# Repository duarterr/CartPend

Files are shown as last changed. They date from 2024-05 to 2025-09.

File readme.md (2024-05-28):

# Pendulum on a Cart Project

Welcome to the Pendulum on a Cart project repository! This project involves designing, modeling, and controlling a pendulum attached to a cart. The system is a classic example of a dynamic system that can be used to explore control theory and robotics concepts.

## Repository Structure

The repository is organized into the following folders:

- **Design Files**: Contains the Fusion360 model and other related files for the physical construction of the pendulum on a cart.
- **Matlab**: Contains scripts for modeling the system, validating the model, and designing the controller.
- **CodeComposerStudio**: Contains code for the TivaC TM4C123GH6PM microcontroller used to implement the control algorithms.
- **References**: Contains useful references that provide the theoretical background for the project.

## Contents

### Design Files

This directory contains all the necessary files for the physical design and construction of the pendulum on a cart. 

- **Fusion360 Model**: The 3D model of the pendulum on a cart created using Autodesk Fusion360.
- **Additional Design Files**: Other files related to the physical construction of the device, such as drawings, part lists, and assembly instructions.

### Matlab

This directory contains MATLAB scripts and resources for various stages of the project:

- **A_Model_Pend_Estimation.m**: Estimates the pendulum model based on experimental data gathered from the device via UART.
- **B_Model_Pend_Validation.m**: Compares the pendulum model with a set of experimental observations.
- **C_Model_Full_Validation.m**: Validates the entire model (pendulum plus cart) by comparing it with experimental data.
- **D_LQR.m**: Designs an LQR (Linear-Quadratic Regulator) controller for the system.

The directory also includes the following subfolders:

- **Datasources**: Contains the experimental data obtained from the device via UART.
- **Functions**: Contains miscellaneous MATLAB functions used in the scripts.
- **Results**: Stores the results from the scripts.

### CodeComposerStudio

This directory contains the code for the TivaC TM4C123GH6PM microcontroller used in the project.

Many functions from [this repository](https://github.com/duarterr/CodeComposerStudio-Libs) are used.

### References

This directory contains references that provide theoretical background and additional information about the pendulum on a cart system.

## Contributions

Contributions to the project are welcome! If you have any improvements or new features to add, please follow these steps:

1. Fork the repository.
2. Create a new branch (`git checkout -b feature-new-feature`).
3. Commit your changes (`git commit -am 'Add new feature'`).
4. Push to the branch (`git push origin feature-new-feature`).
5. Create a new Pull Request.

## License

Anyone is free to use and modify the contentes of this repository, but please provide credit to the author, Renan Duarte.

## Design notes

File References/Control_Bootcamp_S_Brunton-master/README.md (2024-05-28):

# Control_Bootcamp_S_Brunton
Matlab Code by Steven Brunton on his Control Bootcamp Lessons

UTILITIES

cartpend.m           — system of ODEs for inverted pendulum on a cart

drawcartpend.m       — draw inverted pendulum on cart

drawcartpend_bw.m    — draw with inverted colors

PRELIMINARIES

linearize_cartpend.m — test linearized dynamics

sim_cartpend.m       — simulate nonlinear dynamics

CONTROL AND ESTIMATOR DESIGN

poleplace_cartpend.m — pole placement for controllable system

lqr_cartpend.m       — design LQR full-state feedback controller

obsv_cartpend.m      - test observability

kf_cartpend.m        - design Kalman filter for full-state estimation

Simulink implementations of LQR and LQG in folder “simulink_LQR_LQG”

lqg_simulinkINIT.m   — initializes LQR feedback gains and Kalman filter system

lqr_cartpend_sim.slx — simulink model for LQR

lqg_cartpend_sim.slx — simulink model for LQG

cartpend_sim.*       — system block for inverted pendulum on cart

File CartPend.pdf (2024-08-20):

Modelagem Dinamica de um P ˆ | endulo Invertido em um ˆ

# Carro

### Renan Duarte

### 17 de agosto de 2024

Resumo

Este documento apresenta a modelagem dinamica de um p ˆ | endulo invertido montado em um ˆ
carro, um sistema classico utilizado para testar t ´ | ecnicas de controle devido ´ | a sua complexidade `
nao linear. O objetivo principal ˜ | e manter o p ´ | endulo equilibrado na posic¸ ˆ | ao vertical, utilizando ˜

a forc¸a aplicada ao carro como entrada de controle. O documento inicia com a modelagem do

carro, simplificando o problema ao considerar a acelerac¸ao como entrada direta. A modelagem ˜

do pendulo ˆ | e abordada em seguida, com a linearizac¸ ´ | ao das equac¸ ˜ | oes n ˜ | ao lineares para facilitar ˜
a analise. Finalmente, os modelos do carro e do p ´ | endulo s ˆ | ao combinados em um sistema com- ˜

pleto representado no espac¸o de estados. As matrizes de estado sao derivadas e apresentadas, ˜

oferecendo uma visao integrada das din ˜ | amicas do carro e do p ˆ | endulo. Esta abordagem permite ˆ

a analise e o desenvolvimento de controladores para o sistema integrado, fornecendo uma base ´

solida para a implementac¸ ´ | ao de estrat ˜ | egias de controle. ´

## 1 Introduc¸ao˜

O estudo do pendulo invertido montado sobre um carro (IPC) ˆ | e um problema cl ´ | assico em sistemas ´
dinamicos e controle, exemplificando um sistema n ˆ | ao linear com m ˜ | ultiplos graus de liberdade. Este ´
tipo de sistema e frequentemente utilizado para testar e demonstrar t ´ | ecnicas de controle devido ´ | a sua `
dinamica complexa e n ˆ | ao linear. O sistema consiste em um p ˜ | endulo de comprimento ˆ | l e massa m

montado em um carro que se move ao longo de um eixo horizontal. A posic¸ao do carro no eixo ˜

horizontal e denominada ´ | p e o angulo do p ˆ | endulo em relac¸ ˆ | ao˜ a vertical ` | e denotado por ´ | θ, conforme

apresentado na Figura 1.

O objetivo e manter o p ´ | endulo equilibrado na posic¸ ˆ | ao vertical usando a forc¸a atuante no carro ˜ | u

no eixo horizontal como entrada de controle.

m

θ l

p = 0

p

z | u

z = 0

M

Figura 1: Pendulo Invertido em um Carro ˆ

A modelagem desse sistema e fundamental para entender sua din ´ | amica, prever o comportamento ˆ
do pendulo e desenvolver controladores eficientes para estabiliz ˆ | a-lo. ´

## 2 Modelo matematico do carro ´

### 2.1 Equac¸ao do movimento ˜

Vamos iniciar a modelagem pelo carro que suporta o pendulo. Consideramos que o carro se move ˆ

ao longo de um eixo horizontal e que sua dinamica ˆ | e governada pela segunda lei de Newton. ´
A equac¸ao do movimento do carro ˜ | e dada por (1). ´

M

d

2p
dt²
= Fa + Fr − Fp | (1)

Onde:

- p e a posic¸ ´ | ao do carro no eixo horizontal [m]. ˜
- M e a massa do carro [kg]. ´
- Fa e a forc¸a resultante da acelerac¸ ´ | ao aplicada ao carro [N]. ˜
- Fr e a soma das forc¸as resistivas, incluindo o atrito e a resist ´ | encia do ar [N]. ˆ
- Fp e a forc¸a horizontal exercida pelo p ´ | endulo no ponto de suporte, que depende do ˆ | angulo ˆ | θ e

da velocidade angular ω [N].

Modelar os coeficientes que afetam o movimento do carro, como o atrito entre o carro e o trilho,

a resistencia do ar, e as interac¸ ˆ | oes din ˜ | amicas com o p ˆ | endulo, pode ser uma tarefa complexa e sujeita ˆ
a incertezas. Esses coeficientes sao influenciados por diversos fatores, como variac¸ ˜ | oes na superf ˜ | ´ıcie
do trilho, mudanc¸as nas condic¸oes ambientais, e at ˜ | e mesmo a forma como o p ´ | endulo oscila. Devido a ˆ

essa complexidade, obter valores precisos para esses coeficientes pode ser desafiador e pode introduzir

erros no modelo.

Para simplificar a modelagem do movimento do carro, consideramos como entrada (ou variavel ´

de controle) a acelerac¸ao˜ a, que e aplicada diretamente ao carro. Essa suposic¸ ´ | ao˜ e razo ´ | avel quando o ´

sistema possui um motor com torque suficiente para impor a acelerac¸ao desejada, sem que as forc¸as re- ˜

sistivas interfiram significativamente. Com essa simplificac¸ao, podemos focar na an ˜ | alise da din ´ | amica ˆ
do carro em resposta a acelerac¸ ` | ao aplicada, sem a necessidade de modelar explicitamente as forc¸as ˜
de propulsao e resist ˜ | encia que poderiam complicar o sistema. ˆ

### 2.2 Representac¸ao em espac¸o de estados ˜

Para modelar o comportamento do carro em espac¸o de estados, devemos primeiro definir os es-

tados do sistema, que sao as vari ˜ | aveis necess ´ | arias para descrever completamente sua din ´ | amica em ˆ

qualquer instante de tempo. No caso do carro, podemos escolher os seguintes estados:

- x1 = p: A posic¸ao do carro ao longo do eixo horizontal [m]. ˜
- x2 = v = dp/dt = ˙p: A velocidade do carro [m/s].
Esses dois estados, x1 e x2, sao suficientes para capturar a din ˜ | amica do movimento do carro. ˆ
Utilizando a simplificac¸ao mencionada anteriormente, (1) pode ser reescrita em func¸ ˜ | ao das vari ˜ | aveis ´

de estado do sistema como (2).

x˙2 = a | (2)

A forma geral do modelo de espac¸o de estados e:´

x˙c = Acxc + Bcu | (3)

Onde:

- xc =

h
x1 x2

i⊤
=

h

p vi⊤
e o vetor de estados. ´
- u = a e a entrada do sistema (a acelerac¸ ´ | ao do carro). ˜
- Ac e a matriz que descreve a din ´ | amica do sistema. ˆ
- Bc e a matriz que relaciona a entrada com os estados do sistema. ´

Assim, a reescrita das equac¸oes dos estados na forma matricial resulta nas matrizes ˜ | Ac e Bc dadas
em (4). O modelo dinamico do carro em espac¸o de estados ˆ | e apresentado em 5). ´

Ac =

0 1

0 0

- , Bc =

0

1

- (4)

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
- a | (5)
Essas matrizes capturam a dinamica do carro no espac¸o de estados. A matriz ˆ | Ac define como

os estados do sistema evoluem ao longo do tempo, enquanto a matriz Bc descreve como a entrada

(acelerac¸ao˜ a) influencia os estados.

3 Modelagem matematica do p ´ | endulo ˆ

### 3.1 Equac¸ao do movimento ˜

A equac¸ao do movimento do p ˜ | endulo pode ser derivada a partir do princ ˆ | ´ıpio de conservac¸ao do ˜

momento angular e das forc¸as atuantes no sistema. As principais forc¸as que afetam o movimento do

pendulo incluem a forc¸a gravitacional, a forc¸a de atrito, a resist ˆ | encia do ar e a forc¸a de Coulomb. ˆ

Considerando a soma dos torques em torno do ponto de rotac¸ao e aplicando a segunda lei de ˜

Newton para rotac¸oes, a equac¸ ˜ | ao do movimento do p ˜ | endulo ˆ | e dada por (12). ´

I

d

2
θ
dt²
= τg − τd − τdr − τc + τa | (6)
Essa equac¸ao diferencial n ˜ | ao linear representa a din ˜ | amica angular do p ˆ | endulo em relac¸ ˆ | ao ao ponto ˜

de rotac¸ao, onde: ˜

- θ e o ´ angulo do p ˆ | endulo em relac¸ ˆ | ao˜ a vertical [rad]. `
- I e o momento de in ´ | ercia do p ´ | endulo em relac¸ ˆ | ao ao ponto de rotac¸ ˜ | ao [ ˜ | kg · m²
].
- τg e o torque em torno do ponto de rotac¸ ´ | ao devido ˜ | a forc¸a gravitacional [Nm]. `
- τd e o torque causado pelo atrito linear do eixo de rotac¸ ´ | ao que resiste ao movimento do p ˜ | endulo ˆ

[Nm].

- τdr e o torque causado pela resist ´ | encia do ar [Nm]. ˆ
- τc e o torque causado pela forc¸a de Coulomb [Nm]. ´

- τa e o torque devido ao movimento do carro [Nm]. ´

Os termos τg, τd, τdr, τc e τg sao dados em (7-11). ˜

τg = mglsin(θ) | (7)
τd = Kdω | (8)

τdr = Kdrω

2
(9)
τc = Kc · sign(ω) | (10)
τa = ml cos(θ) · a | (11)

Nestas equac¸oes: ˜

- ω e a velocidade angular do p ´ | endulo ( ˆ

˙θ) [rad/s].

- l e o comprimento do p ´ | endulo [m]. ˆ
- m e massa do p ´ | endulo [kg]. ˆ
- Kd e coeficiente de atrito linear no ponto de suspens ´ | ao [ ˜ | N · s/m].
- Kdr e o coeficiente de resist ´ | encia do ar [ ˆ | N · s

2/m²
].
- Kc e a forc¸a de Coulomb [N]. ´
Assim, a equac¸ao do movimento do p ˜ | endulo pode ser reescrita como em (12). ˆ

I

d

2
θ
dt²

= mglsin(θ) − Kdω − Kdrω

| 2 − Kc · sign(ω) + mla cos(θ) | (12)

### 3.2 Representac¸ao em espac¸o de estados ˜

Para obter uma representac¸ao em espac¸o de estados linear de um sistema n ˜ | ao linear, precisamos ˜
linearizar as equac¸oes que descrevem seu comportamento din ˜ | amico ao redor de um ponto de operac¸ ˆ | ao˜

(ou ponto de equil´ıbrio).

No caso do pendulo, temos dois poss ˆ | ´ıveis pontos de equil´ıbrio: θ = 0 (pendulo para cima) e ˆ | θ = π

(pendulo para baixo). ˆ

Como nosso objetivo de controle e equilibrar o p ´ | endulo na vertical, faremos a linearizac¸ ˆ | ao em ˜

torno do ponto θ = 0.

O processo de linearizac¸ao envolve a expans ˜ | ao da func¸ ˜ | ao n ˜ | ao linear em torno do ponto de operac¸ ˜ | ao˜
usando uma serie de Taylor e a simplificac¸ ´ | ao dos termos n ˜ | ao lineares. Para pequenas perturbac¸ ˜ | oes ˜

ao redor desse ponto, os termos de ordem superior (como sin(θ) e cos(θ) sao aproximados por suas ˜

versoes lineares. A partir dessa aproximac¸ ˜ | ao, obtemos um sistema linearizado que pode ser represen- ˜

tado no espac¸o de estados, permitindo a analise e o design de controladores com maior simplicidade ´

e precisao. ˜

Para pequenas perturbac¸oes em torno de ˜ | θ = 0, os termos nao lineares de (12) ser ˜ | ao: ˜
- sin(θ) ≈ 0
- cos(θ) ≈ 1
- ω

2 ≈ 0

- sign(ω) ≈ 0

Assim, o modelo linearizado em torno do ponto θ = 0 e dado em (13). ´

I

d

2
θ
dt²
≈ mglθ − Kdω + mla | (13)
Para representa-lo em espac¸o de estados, primeiramente definimos os os estados necess ´ | arios para ´
representar o comportamento do sistema. Para o pendulo, os estados s ˆ | ao definidos como: ˜
- x1 = θ: O angulo do p ˆ | endulo em relac¸ ˆ | ao˜ a vertical [rad]. `
- x2 = ω = ˙θ: A velocidade angular do pendulo [rad/s]. ˆ

Dessa forma, (13) pode ser reescrita em func¸ao dos estados do sistema como (14). ˜

x˙2 ≈

mgl
I

x1 −

Kd
I

x2 +

ml
I
a | (14)
Assim, a reescrita das equac¸oes dos estados na forma matricial resulta nas matrizes ˜ | Ap e Bp dadas
em (15). O modelo dinamico do p ˆ | endulo em espac¸o de estados ˆ | e apresentado em (16). ´

Ap =

0 1

mgl
I −

Kd
I
- , Bp =

0

ml
I
- (15)

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
- a | (16)

## 4 Modelo completo em espac¸o de estados

Para representar o sistema completo, combinamos os modelos do carro e do pendulo. O vetor de ˆ

estados completo pode ser definido como:

x =

h

p v θ ωi⊤
(17)
Assim, as equac¸oes dos estados do sistema completo podem ser ˜ | ao dadas por: ˜

x˙ =

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
(18)

Este sistema pode ser representado na forma matricial x˙ = Ax + Bu com as matrizes A e B

dadas em (19).

A =

Ac 0

### 0 Ap

- , B =

Bc

Bp

- (19)
Dessa forma, o modelo completo do pendulo em um carro, representado em espac¸o de estados ˆ | e´

dado em (20).

p˙

v˙

˙θ

ω˙

=

0 1 | 0 | 0
0 0 | 0 | 0
0 0 | 0 | 1

0 0 mgl
| I | − Kd I

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
a | (20)
Neste modelo completo, u = a e a acelerac¸ ´ | ao aplicada ao carro e afeta tanto o carro quanto o ˜
pendulo. A matriz ˆ | A captura a dinamica combinada do carro e do p ˆ | endulo, enquanto a matriz ˆ | B

descreve como a entrada (acelerac¸ao) influencia o sistema. ˜

| Dessa forma, temos uma representac¸ao completa do sistema em espac¸o de estados que permite a ˜
analise e o design de controladores para o sistema integrado carro-p ´ | endulo. ˆ

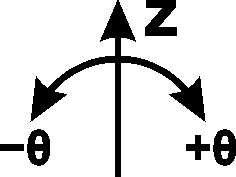
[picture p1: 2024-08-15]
Design Files/LaserCut_0.3mm_Kerf/Cart/Engrave_Body_2.bmp

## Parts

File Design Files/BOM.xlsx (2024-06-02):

These are the main items. There are other miscellaneous stuff
Item | Qty | Price Un | Total Price | URL
Aluminum profile T20 x 600mm | 2 | R$24.20 | R$48.40 | https://shopee.com.br/Perfil-Estrutural-em-Alum%C3%ADnio-20x20-T-Slot-Canal-6mm-Modelo-Misumi-Voron-i.372671323.11243829361
MGN9H 450mm rail + Block | 1 | R$90.76 | R$90.76 | https://www.aliexpress.com/item/32908785875.html
Nema 17 motor | 1 | R$52.63 | R$52.63 | https://www.aliexpress.com/item/1005005642034164.html
1000 PPR encoder | 2 | R$58.49 | R$116.98 | https://www.aliexpress.com/item/1005005779039462.html
NC panel buttons | 2 |  | R$0.00
DRV8823 stepper driver board | 1 | R$14.50 | R$14.50 | https://shopee.com.br/Driver-Motor-Passo-DRV-8825-com-Dissipador-3D-Laser-i.809429142.20297657307
8mmX6.1mmx500mm carbon fiber tube | 1 | R$10.05 | R$10.05
3mm A3 MDF sheet | 1 |  | R$0.00
 |  |  | R$0.00
T Shape Hammer Block Sliding Nut Screw M3 M4 M5 Kit | 1 | R$27.10 | R$27.10 | https://www.aliexpress.com/item/1005006408212570.html
5M Gt2 Timing Belt 6mm Wide Replacement Kit | 1 | R$27.47 | R$27.47 | https://www.aliexpress.com/item/1005003025464689.html

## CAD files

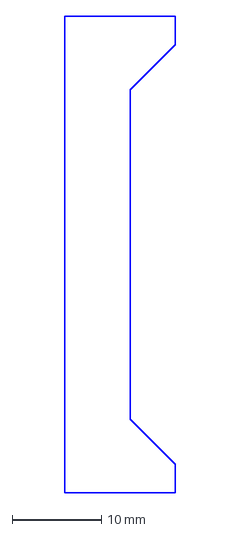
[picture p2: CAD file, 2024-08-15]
Design Files/LaserCut_0.3mm_Kerf/Cart/Suporte Theta - Body9.dxf
12.3 x 53.3 mm

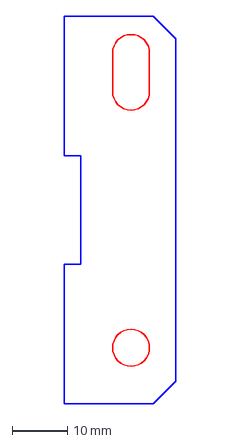
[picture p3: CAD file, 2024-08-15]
Design Files/LaserCut_0.3mm_Kerf/Eletronicos/Support Electronics - Body3.dxf
20.3 x 70.3 mm

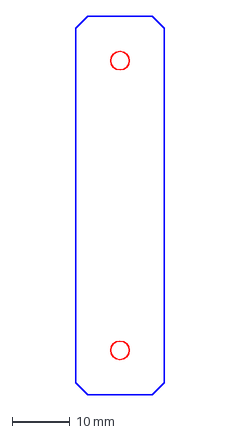
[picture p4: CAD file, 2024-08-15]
Design Files/LaserCut_0.3mm_Kerf/Frame/Pe - Body2 (2).dxf
15.3 x 65.3 mm

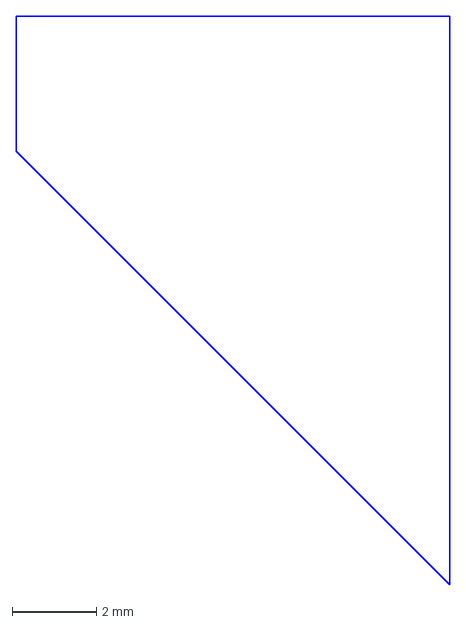
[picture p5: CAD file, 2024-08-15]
Design Files/LaserCut_0.3mm_Kerf/Motor/Support Motor - Body5.dxf
10.3 x 13.5 mm

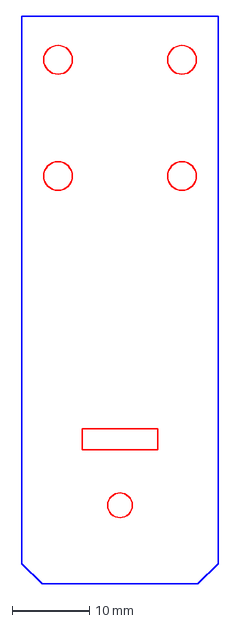
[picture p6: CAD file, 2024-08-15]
Design Files/LaserCut_0.3mm_Kerf/Cart/Suporte Theta - Body10.dxf
25.3 x 73.3 mm

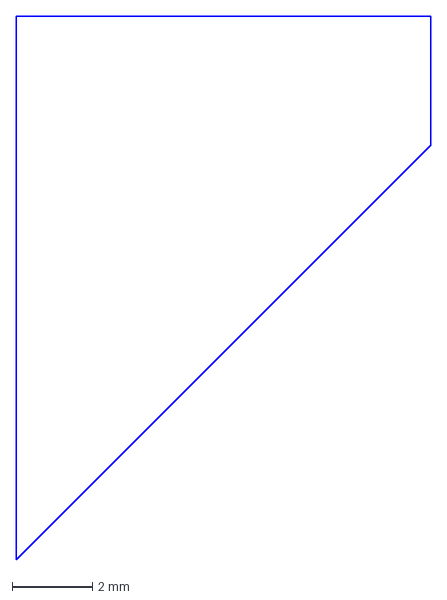
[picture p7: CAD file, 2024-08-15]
Design Files/LaserCut_0.3mm_Kerf/Eletronicos/Support Electronics - Body5.dxf
10.3 x 13.5 mm

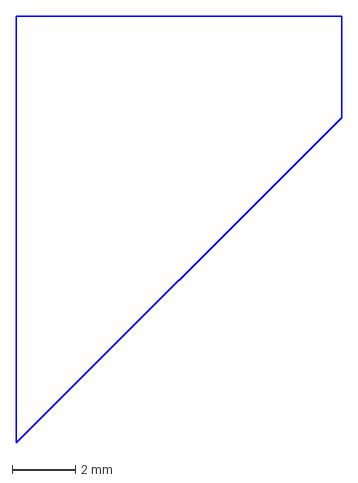
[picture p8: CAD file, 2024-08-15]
Design Files/LaserCut_0.3mm_Kerf/Motor/Support Motor - Body4.dxf
10.3 x 13.5 mm

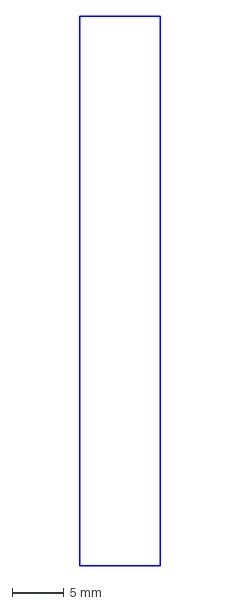
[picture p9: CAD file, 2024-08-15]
Design Files/LaserCut_0.3mm_Kerf/Cart/Suporte Theta - Body16.dxf
7.80 x 53.3 mm

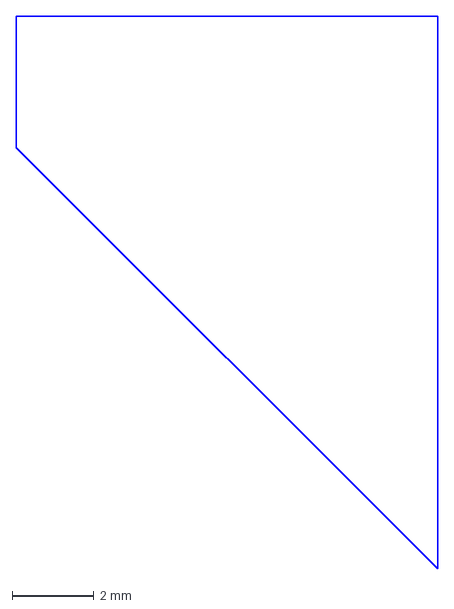
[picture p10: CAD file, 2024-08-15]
Design Files/LaserCut_0.3mm_Kerf/Eletronicos/Support Electronics - Body4.dxf
10.3 x 13.5 mm

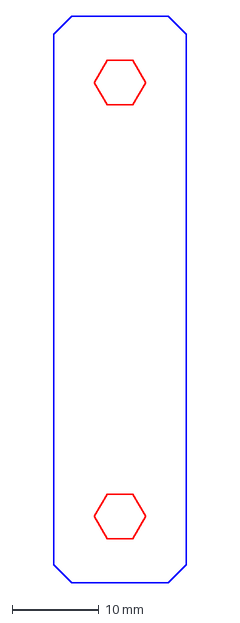
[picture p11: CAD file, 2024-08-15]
Design Files/LaserCut_0.3mm_Kerf/Frame/Pe - Body1 (1).dxf
15.3 x 65.3 mm

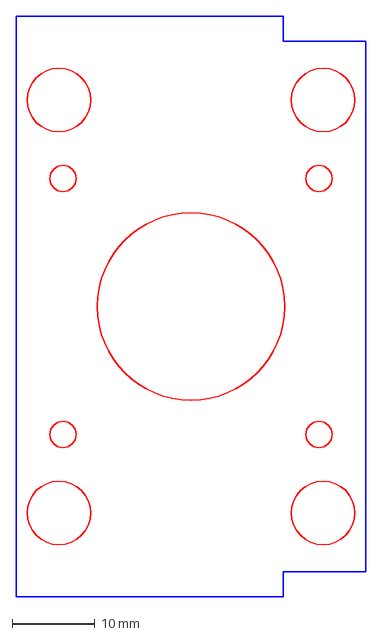
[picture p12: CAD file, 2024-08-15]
Design Files/LaserCut_0.3mm_Kerf/Motor/Support Motor - Body2.dxf
42.3 x 70.3 mm

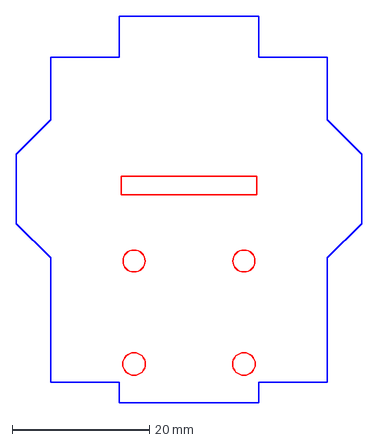
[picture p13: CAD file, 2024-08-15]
Design Files/LaserCut_0.3mm_Kerf/Cart/Suporte Theta - Body4.dxf
50.3 x 56.3 mm

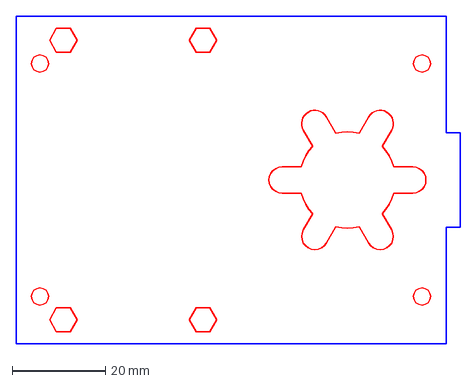
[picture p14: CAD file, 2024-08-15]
Design Files/LaserCut_0.3mm_Kerf/Eletronicos/Support Electronics - Body1.dxf
95.3 x 70.3 mm

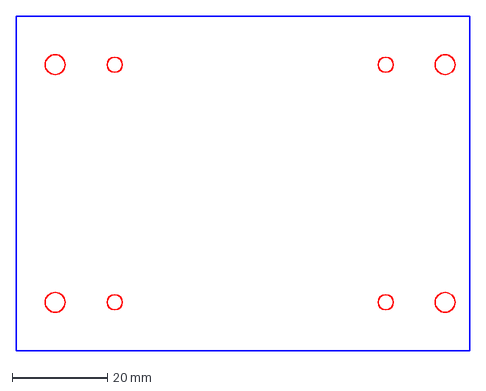
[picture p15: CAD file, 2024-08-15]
Design Files/LaserCut_0.3mm_Kerf/Frame/Inferior Support Electronics - Body1.dxf
95.3 x 70.3 mm

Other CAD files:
Design Files/LaserCut_0.3mm_Kerf/Motor/Support Motor - Body3.dxf
Design Files/LaserCut_0.3mm_Kerf/Cart/Suporte Theta - Body17.dxf
Design Files/LaserCut_0.3mm_Kerf/Eletronicos/Support Electronics - Body2.dxf
Design Files/LaserCut_0.3mm_Kerf/Cart/Suporte Theta - Body1.dxf
Design Files/LaserCut_0.3mm_Kerf/Cart/Suporte Theta - Body11.dxf
Design Files/LaserCut_0.3mm_Kerf/Cart/Suporte Theta - Body13.dxf
Design Files/LaserCut_0.3mm_Kerf/Cart/Suporte Theta - Body2.dxf
Design Files/LaserCut_0.3mm_Kerf/Cart/Suporte Theta - Body5.dxf
Design Files/LaserCut_0.3mm_Kerf/Cart/Suporte Theta - Body6.dxf
Design Files/LaserCut_0.3mm_Kerf/Cart/Suporte Theta - Body7.dxf
Design Files/LaserCut_0.3mm_Kerf/Frame/Inferior Support Motor - Body1.dxf
Design Files/LaserCut_0.3mm_Kerf/Frame/Lateral Support - Body1.dxf
Design Files/LaserCut_0.3mm_Kerf/Frame/Lateral Support - Body2.dxf
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

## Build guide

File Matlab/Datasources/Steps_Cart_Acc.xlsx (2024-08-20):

 |  |  |  |  |  |  | Time | Tick | Accel | CurrentPPS | Pos | PosDot | Theta | ThetaDot
24533 | 0 | 0 | 0.164698 | 0.00995 | 3.141593 | 0 | 0 | 0 | 0 | 0 | 0.164698 | 0 | 3.141593 | 0
24553 | 0 | 0 | 0.164698 | 0.00995 | 3.141593 | 0 | 0.02 | 20 | 0 | 0 | 0.164698 | 0 | 3.141593 | 0
24573 | 0 | 0 | 0.164698 | 0.00995 | 3.141593 | 0 | 0.04 | 40 | 0 | 0 | 0.164698 | 0 | 3.141593 | 0
24593 | 0 | 0 | 0.164698 | 0.00995 | 3.141593 | 0 | 0.06 | 60 | 0 | 0 | 0.164698 | 0 | 3.141593 | 0
24613 | 0 | 0 | 0.164698 | 0.00995 | 3.141593 | 0 | 0.08 | 80 | 0 | 0 | 0.164698 | 0 | 3.141593 | 0
24633 | 0 | 0 | 0.164698 | 0.00995 | 3.141593 | 0 | 0.1 | 100 | 0 | 0 | 0.164698 | 0 | 3.141593 | 0
24653 | 0 | 0 | 0.164698 | 0.00995 | 3.141593 | 0 | 0.12 | 120 | 0 | 0 | 0.164698 | 0 | 3.141593 | 0
24673 | 0 | 0 | 0.164698 | 0.00995 | 3.141593 | 0 | 0.14 | 140 | 0 | 0 | 0.164698 | 0 | 3.141593 | 0
24693 | 0 | 0 | 0.164698 | 0.00995 | 3.141593 | 0 | 0.16 | 160 | 0 | 0 | 0.164698 | 0 | 3.141593 | 0
24713 | 0 | 0 | 0.164698 | 0.00995 | 3.141593 | 0 | 0.18 | 180 | 0 | 0 | 0.164698 | 0 | 3.141593 | 0
24733 | 0 | 0 | 0.164698 | 0.00995 | 3.141593 | 0 | 0.2 | 200 | 0 | 0 | 0.164698 | 0 | 3.141593 | 0
24753 | 0 | 0 | 0.164698 | 0.00995 | 3.141593 | 0 | 0.22 | 220 | 0 | 0 | 0.164698 | 0 | 3.141593 | 0
24773 | 0 | 0 | 0.164698 | 0.00995 | 3.141593 | 0 | 0.24 | 240 | 0 | 0 | 0.164698 | 0 | 3.141593 | 0
24793 | 0 | 0 | 0.164698 | 0.00995 | 3.141593 | 0 | 0.26 | 260 | 0 | 0 | 0.164698 | 0 | 3.141593 | 0
24813 | 0 | 0 | 0.164698 | 0.00995 | 3.141593 | 0 | 0.28 | 280 | 0 | 0 | 0.164698 | 0 | 3.141593 | 0
24833 | 0 | 0 | 0.164698 | 0.00995 | 3.141593 | 0 | 0.3 | 300 | 0 | 0 | 0.164698 | 0 | 3.141593 | 0
24853 | 0 | 0 | 0.164698 | 0.00995 | 3.141593 | 0 | 0.32 | 320 | 0 | 0 | 0.164698 | 0 | 3.141593 | 0
24873 | 0 | 0 | 0.164698 | 0.00995 | 3.141593 | 0 | 0.34 | 340 | 0 | 0 | 0.164698 | 0 | 3.141593 | 0
24893 | 0 | 0 | 0.164698 | 0.00995 | 3.141593 | 0 | 0.36 | 360 | 0 | 0 | 0.164698 | 0 | 3.141593 | 0
24913 | 0 | 0 | 0.164698 | 0.00995 | 3.141593 | 0 | 0.38 | 380 | 0 | 0 | 0.164698 | 0 | 3.141593 | 0
24933 | 0 | 0 | 0.164698 | 0.00995 | 3.141593 | 0 | 0.4 | 400 | 0 | 0 | 0.164698 | 0 | 3.141593 | 0
24953 | 0 | 0 | 0.164698 | 0.00995 | 3.141593 | 0 | 0.42 | 420 | 0 | 0 | 0.164698 | 0 | 3.141593 | 0
24973 | 0 | 0 | 0.164698 | 0.00995 | 3.141593 | 0 | 0.44 | 440 | 0 | 0 | 0.164698 | 0 | 3.141593 | 0
24993 | -1 | -869 | 0.164688 | -0.01194 | 3.141593 | 0 | 0.46 | 460 | -1 | -869 | 0.164688 | -0.02189 | 3.141593 | 0
25013 | -1 | -3418 | 0.164588 | 0.029849 | 3.141593 | 0 | 0.48 | 480 | -1 | -3418 | 0.164588 | 0.019899 | 3.141593 | 0
25033 | -1 | -6109 | 0.164061 | -0.035819 | 3.141593 | 0.314159 | 0.5 | 500 | -1 | -6109 | 0.164061 | -0.045769 | 3.141593 | 0.314159
25053 | -1 | -8799 | 0.163205 | -0.061688 | 3.138451 | -0.314159 | 0.52 | 520 | -1 | -8799 | 0.163205 | -0.071638 | 3.138451 | -0.314159
25073 | -1 | -11490 | 0.162121 | -0.067658 | 3.13688 | 0 | 0.54 | 540 | -1 | -11490 | 0.162121 | -0.077608 | 3.13688 | 0
25093 | -1 | -14180 | 0.16027 | -0.089547 | 3.133739 | 0 | 0.56 | 560 | -1 | -14180 | 0.16027 | -0.099497 | 3.133739 | 0
25113 | -1 | -16729 | 0.158012 | -0.103477 | 3.129026 | -0.314159 | 0.58 | 580 | -1 | -16729 | 0.158012 | -0.113427 | 3.129026 | -0.314159
25133 | -1 | -19420 | 0.155345 | -0.129346 | 3.124314 | -0.314159 | 0.6 | 600 | -1 | -19420 | 0.155345 | -0.139296 | 3.124314 | -0.314159
25153 | -1 | -22110 | 0.152877 | -0.137306 | 3.119601 | -0.314159 | 0.62 | 620 | -1 | -22110 | 0.152877 | -0.147256 | 3.119601 | -0.314159
25173 | -1 | -24801 | 0.150121 | -0.151236 | 3.11646 | 0 | 0.64 | 640 | -1 | -24801 | 0.150121 | -0.161186 | 3.11646 | 0
25193 | -1 | -27492 | 0.146221 | -0.169145 | 3.108606 | -0.314159 | 0.66 | 660 | -1 | -27492 | 0.146221 | -0.179095 | 3.108606 | -0.314159
25213 | -1 | -30041 | 0.141873 | -0.185065 | 3.102323 | -0.314159 | 0.68 | 680 | -1 | -30041 | 0.141873 | -0.195015 | 3.102323 | -0.314159
25233 | 1 | -30465 | 0.137147 | -0.202974 | 3.094469 | -0.314159 | 0.7 | 700 | 1 | -30465 | 0.137147 | -0.212924 | 3.094469 | -0.314159
25253 | 1 | -27775 | 0.133416 | -0.191035 | 3.088186 | -0.628319 | 0.72 | 720 | 1 | -27775 | 0.133416 | -0.200985 | 3.088186 | -0.628319
25273 | 1 | -25084 | 0.129993 | -0.177105 | 3.085044 | 0 | 0.74 | 740 | 1 | -25084 | 0.129993 | -0.187055 | 3.085044 | 0
25293 | 1 | -22394 | 0.126162 | -0.151236 | 3.080332 | -0.314159 | 0.76 | 760 | 1 | -22394 | 0.126162 | -0.161186 | 3.080332 | -0.314159
25313 | 1 | -19845 | 0.12271 | -0.137306 | 3.078761 | 0 | 0.78 | 780 | 1 | -19845 | 0.12271 | -0.147256 | 3.078761 | 0
25333 | 1 | -17154 | 0.119665 | -0.123377 | 3.07719 | 0 | 0.8 | 800 | 1 | -17154 | 0.119665 | -0.133327 | 3.07719 | 0
25353 | 1 | -14464 | 0.117576 | -0.111437 | 3.07719 | 0 | 0.82 | 820 | 1 | -14464 | 0.117576 | -0.121387 | 3.07719 | 0
25373 | 1 | -11773 | 0.115845 | -0.093527 | 3.078761 | 0 | 0.84 | 840 | 1 | -11773 | 0.115845 | -0.103477 | 3.078761 | 0
25393 | 1 | -9082 | 0.114024 | -0.077608 | 3.081902 | 0 | 0.86 | 860 | 1 | -9082 | 0.114024 | -0.087558 | 3.081902 | 0
25413 | 1 | -6534 | 0.112671 | -0.063678 | 3.088186 | 0.314159 | 0.88 | 880 | 1 | -6534 | 0.112671 | -0.073628 | 3.088186 | 0.314159
25433 | 1 | -3843 | 0.111725 | -0.039799 | 3.094469 | 0.314159 | 0.9 | 900 | 1 | -3843 | 0.111725 | -0.049749 | 3.094469 | 0.314159
25453 | 1 | -1152 | 0.111308 | -0.021889 | 3.099181 | 0 | 0.92 | 920 | 1 | -1152 | 0.111308 | -0.031839 | 3.099181 | 0
25473 | 1 | 1537 | 0.111238 | -0.01592 | 3.107035 | 0.314159 | 0.94 | 940 | 1 | 1537 | 0.111238 | -0.02587 | 3.107035 | 0.314159
25493 | 1 | 4228 | 0.111516 | 0.035819 | 3.11646 | 0.314159 | 0.96 | 960 | 1 | 4228 | 0.111516 | 0.025869 | 3.11646 | 0.314159
25513 | 1 | 6777 | 0.112213 | 0.041789 | 3.129026 | 0.628319 | 0.98 | 980 | 1 | 6777 | 0.112213 | 0.031839 | 3.129026 | 0.628319
25533 | 1 | 9467 | 0.113327 | 0.059698 | 3.140022 | 0.314159 | 1 | 1000 | 1 | 9467 | 0.113327 | 0.049748 | 3.140022 | 0.314159
25553 | 1 | 12158 | 0.114581 | 0.081588 | -3.133739 | 0.628319 | 1.02 | 1020 | 1 | 12158 | 0.114581 | 0.071638 | 3.149446307 | 0.628319
25573 | 1 | 14848 | 0.116123 | 0.089547 | -3.122743 | 0.628319 | 1.04 | 1040 | 1 | 14848 | 0.116123 | 0.079597 | 3.160442307 | 0.628319
25593 | 1 | 17539 | 0.118461 | 0.113427 | -3.108606 | 0.628319 | 1.06 | 1060 | 1 | 17539 | 0.118461 | 0.103477 | 3.174579307 | 0.628319
25613 | 1 | 20088 | 0.121237 | 0.125366 | -3.094469 | 0.628319 | 1.08 | 1080 | 1 | 20088 | 0.121237 | 0.115416 | 3.188716307 | 0.628319
25633 | 1 | 22779 | 0.124401 | 0.145266 | -3.080332 | 0.314159 | 1.1 | 1100 | 1 | 22779 | 0.124401 | 0.135316 | 3.202853307 | 0.314159
25653 | 1 | 25469 | 0.127287 | 0.157206 | -3.067765 | 0.628319 | 1.12 | 1120 | 1 | 25469 | 0.127287 | 0.147256 | 3.215420307 | 0.628319
25673 | 1 | 28160 | 0.130441 | 0.173125 | -3.055199 | 0.942478 | 1.14 | 1140 | 1 | 28160 | 0.130441 | 0.163175 | 3.227986307 | 0.942478
25693 | -1 | 30567 | 0.134839 | 0.195015 | -3.041062 | 0.628319 | 1.16 | 1160 | -1 | 30567 | 0.134839 | 0.185065 | 3.242123307 | 0.628319
25713 | -1 | 28018 | 0.139465 | 0.195015 | -3.026925 | 0.628319 | 1.18 | 1180 | -1 | 28018 | 0.139465 | 0.185065 | 3.256260307 | 0.628319
25733 | -1 | 25327 | 0.143803 | 0.173125 | -3.014358 | 0.628319 | 1.2 | 1200 | -1 | 25327 | 0.143803 | 0.163175 | 3.268827307 | 0.628319
25753 | -1 | 22637 | 0.146937 | 0.161185 | -3.006504 | 0.314159 | 1.22 | 1220 | -1 | 22637 | 0.146937 | 0.151235 | 3.276681307 | 0.314159
25773 | -1 | 19946 | 0.149743 | 0.143276 | -3.000221 | 0.314159 | 1.24 | 1240 | -1 | 19946 | 0.149743 | 0.133326 | 3.282964307 | 0.314159
25793 | -1 | 17256 | 0.152828 | 0.125366 | -2.995509 | 0.314159 | 1.26 | 1260 | -1 | 17256 | 0.152828 | 0.115416 | 3.287676307 | 0.314159
25813 | -1 | 14707 | 0.155484 | 0.113427 | -2.992367 | 0 | 1.28 | 1280 | -1 | 14707 | 0.155484 | 0.103477 | 3.290818307 | 0
25833 | -1 | 12016 | 0.157683 | 0.089547 | -2.992367 | 0 | 1.3 | 1300 | -1 | 12016 | 0.157683 | 0.079597 | 3.290818307 | 0
25853 | -1 | 9326 | 0.159126 | 0.077608 | -2.993938 | 0 | 1.32 | 1320 | -1 | 9326 | 0.159126 | 0.067658 | 3.289247307 | 0
25873 | -1 | 6635 | 0.16026 | 0.061688 | -2.997079 | 0 | 1.34 | 1340 | -1 | 6635 | 0.16026 | 0.051738 | 3.286106307 | 0
25893 | -1 | 3945 | 0.161245 | 0.041789 | -3.004933 | -0.314159 | 1.36 | 1360 | -1 | 3945 | 0.161245 | 0.031839 | 3.278252307 | -0.314159
25913 | -1 | 1396 | 0.161812 | 0.029849 | -3.012787 | -0.314159 | 1.38 | 1380 | -1 | 1396 | 0.161812 | 0.019899 | 3.270398307 | -0.314159
25933 | 0 | 0 | 0.161872 | -0.01393 | -3.025354 | -0.628319 | 1.4 | 1400 | 0 | 0 | 0.161872 | -0.02388 | 3.257831307 | -0.628319
25953 | 0 | 0 | 0.161872 | 0.00995 | -3.034779 | -0.314159 | 1.42 | 1420 | 0 | 0 | 0.161872 | 0 | 3.248406307 | -0.314159
25973 | 0 | 0 | 0.161872 | 0.00995 | -3.047345 | -0.628319 | 1.44 | 1440 | 0 | 0 | 0.161872 | 0 | 3.235840307 | -0.628319
25993 | 0 | 0 | 0.161872 | 0.00995 | -3.061482 | -0.628319 | 1.46 | 1460 | 0 | 0 | 0.161872 | 0 | 3.221703307 | -0.628319
26013 | 0 | 0 | 0.161872 | 0.00995 | -3.07719 | -0.628319 | 1.48 | 1480 | 0 | 0 | 0.161872 | 0 | 3.205995307 | -0.628319
26033 | 0 | 0 | 0.161872 | 0.00995 | -3.094469 | -0.628319 | 1.5 | 1500 | 0 | 0 | 0.161872 | 0 | 3.188716307 | -0.628319
26053 | 0 | 0 | 0.161872 | 0.00995 | -3.108606 | -0.628319 | 1.52 | 1520 | 0 | 0 | 0.161872 | 0 | 3.174579307 | -0.628319
26073 | 0 | 0 | 0.161872 | 0.00995 | -3.122743 | -0.628319 | 1.54 | 1540 | 0 | 0 | 0.161872 | 0 | 3.160442307 | -0.628319
26093 | 0 | 0 | 0.161872 | 0.00995 | -3.140022 | -0.628319 | 1.56 | 1560 | 0 | 0 | 0.161872 | 0 | 3.143163307 | -0.628319
26113 | 0 | 0 | 0.161872 | 0.00995 | 3.125885 | -0.942478 | 1.58 | 1580 | 0 | 0 | 0.161872 | 0 | 3.125885 | -0.942478
26133 | 0 | 0 | 0.161872 | 0.00995 | 3.108606 | -0.628319 | 1.6 | 1600 | 0 | 0 | 0.161872 | 0 | 3.108606 | -0.628319
26153 | 0 | 0 | 0.161872 | 0.00995 | 3.094469 | -0.628319 | 1.62 | 1620 | 0 | 0 | 0.161872 | 0 | 3.094469 | -0.628319
26173 | 0 | 0 | 0.161872 | 0.00995 | 3.081902 | -0.628319 | 1.64 | 1640 | 0 | 0 | 0.161872 | 0 | 3.081902 | -0.628319
26193 | 0 | 0 | 0.161872 | 0.00995 | 3.064624 | -0.628319 | 1.66 | 1660 | 0 | 0 | 0.161872 | 0 | 3.064624 | -0.628319
26213 | 0 | 0 | 0.161872 | 0.00995 | 3.050486 | -0.314159 | 1.68 | 1680 | 0 | 0 | 0.161872 | 0 | 3.050486 | -0.314159
26233 | 0 | 0 | 0.161872 | 0.00995 | 3.034778 | -0.628319 | 1.7 | 1700 | 0 | 0 | 0.161872 | 0 | 3.034778 | -0.628319
26253 | 0 | 0 | 0.161872 | 0.00995 | 3.025354 | -0.314159 | 1.72 | 1720 | 0 | 0 | 0.161872 | 0 | 3.025354 | -0.314159
26273 | 0 | 0 | 0.161872 | 0.00995 | 3.015929 | -0.314159 | 1.74 | 1740 | 0 | 0 | 0.161872 | 0 | 3.015929 | -0.314159
26293 | 0 | 0 | 0.161872 | 0.00995 | 3.004934 | -0.314159 | 1.76 | 1760 | 0 | 0 | 0.161872 | 0 | 3.004934 | -0.314159
26313 | 0 | 0 | 0.161882 | 0.00995 | 2.995508 | -0.314159 | 1.78 | 1780 | 0 | 0 | 0.161882 | 0 | 2.995508 | -0.314159
26333 | 0 | 0 | 0.161882 | 0.00995 | 2.989226 | 0 | 1.8 | 1800 | 0 | 0 | 0.161882 | 0 | 2.989226 | 0
26353 | 0 | 0 | 0.161882 | 0.00995 | 2.984513 | 0 | 1.82 | 1820 | 0 | 0 | 0.161882 | 0 | 2.984513 | 0
26373 | 0 | 0 | 0.161882 | 0.00995 | 2.9798 | -0.314159 | 1.84 | 1840 | 0 | 0 | 0.161882 | 0 | 2.9798 | -0.314159
26393 | 0 | 0 | 0.161862 | -0.01393 | 2.97823 | 0 | 1.86 | 1860 | 0 | 0 | 0.161862 | -0.02388 | 2.97823 | 0
26413 | 0 | 0 | 0.161832 | 0.01393 | 2.97823 | 0 | 1.88 | 1880 | 0 | 0 | 0.161832 | 0.00398 | 2.97823 | 0
26433 | 0 | 0 | 0.161832 | 0.00995 | 2.97823 | 0 | 1.9 | 1900 | 0 | 0 | 0.161832 | 0 | 2.97823 | 0
26453 | 0 | 0 | 0.161832 | 0.00995 | 2.981372 | 0 | 1.92 | 1920 | 0 | 0 | 0.161832 | 0 | 2.981372 | 0
26473 | 0 | 0 | 0.161832 | 0.00995 | 2.984513 | 0 | 1.94 | 1940 | 0 | 0 | 0.161832 | 0 | 2.984513 | 0
26493 | 0 | 0 | 0.161832 | 0.00995 | 2.992367 | 0.314159 | 1.96 | 1960 | 0 | 0 | 0.161832 | 0 | 2.992367 | 0.314159
26513 | 0 | 0 | 0.161832 | 0.00995 | 3.000221 | 0.314159 | 1.98 | 1980 | 0 | 0 | 0.161832 | 0 | 3.000221 | 0.314159
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

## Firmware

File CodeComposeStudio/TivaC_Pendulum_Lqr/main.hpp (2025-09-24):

// ------------------------------------------------------------------------------------------------------- //
// Pendulum on a cart
// ------------------------------------------------------------------------------------------------------- //

// Version: 1.0
// Author: Renan Duarte
// E-mail: duarte.renan@hotmail.com
// Date:   13/05/2024
// Device: CORTEX M4F TM4C123GH6PM Tiva C Launchpad

// ------------------------------------------------------------------------------------------------------- //
// Predefined Symbols:
// ------------------------------------------------------------------------------------------------------- //

// PART_TM4C123GH6PM - To use pin_map.h
// TARGET_IS_TM4C129_RA0 - To use the include files in ROM of the Tiva device

// ------------------------------------------------------------------------------------------------------- //
// Pin map
// ------------------------------------------------------------------------------------------------------- //

// Encoder theta
//              PD6     A
//              PD7     B

// Encoder X
//              PC5     A
//              PC6     B

// Stepper
//              PB5     Step
//              PB1     Direction
//              PB0     Enable

// Limit Switches
//              PE2     -X
//              PE3     +X

// LCD
//              PA2     SCLK
//              PA3     DC
//              PA4     SCE
//              PA5     DN
//              PA6     BLK

// Buttons
//              PF4     BTN1
//              PF0     BTN2

// UART
//              PA0     RX
//              PA1     TX

// Extras
//              PF1     RGB_R
//              PF2     RGB_B
//              PF3     RGB_G

// ------------------------------------------------------------------------------------------------------- //

#ifndef MAIN_HPP_
#define MAIN_HPP_

#ifdef __cplusplus
extern "C"
{
#endif

// ------------------------------------------------------------------------------------------------------- //
// Includes
// ------------------------------------------------------------------------------------------------------- //

// LCD functions
#include "Lcd_TivaC.hpp"

// Button functions
#include "Button_TivaC.hpp"

// UART functions
#include "Uart_TivaC.hpp"

// Encoder functions
#include "Encoder_TivaC.hpp"

// RGB LED functions
#include "Rgb_TivaC.hpp"

// Motor functions
#include "DCMotor_TivaC.hpp"

// Auxiliary functions
#include "Aux_Functions.hpp"

// State feedback functions
#include "StateFeedback_TivaC.hpp"

// PID functions
#include "Pid_TivaC.hpp"

// Lead functions
#include "Lead_TivaC.hpp"

// Standard libraries
#include <stdint.h>

// TivaC hardware related libraries
#include "inc/hw_memmap.h"

// TivaC driver libraries
#include "driverlib/fpu.h"
#include "driverlib/gpio.h"
#include "driverlib/interrupt.h"
#include "driverlib/pin_map.h"
#include "driverlib/pwm.h"
#include "driverlib/qei.h"
#include "driverlib/ssi.h"
#include "driverlib/sysctl.h"
#include "driverlib/systick.h"
#include "driverlib/timer.h"
#include "driverlib/uart.h"
#include "driverlib/watchdog.h"

// ------------------------------------------------------------------------------------------------------- //
// Constants
// ------------------------------------------------------------------------------------------------------- //

#define PI                      3.1415926535898F       // Value of Pi

// ------------------------------------------------------------------------------------------------------- //
// Application defines
// ------------------------------------------------------------------------------------------------------- //

// Firmware info
#define DEVICE_FW_NAME          "CARTPEND"             // Firmware name
#define DEVICE_FW_VERSION       "1.0"                  // Firmware version
#define DEVICE_FW_AUTHOR        "Renan Duarte"         // Firmware author

// Application timming
#define TIMER_FREQUENCY         1000                   // Systick timer frequency in Hz
#define CONTROL_LOOP_FREQUENCY  100                    // Control loop frequency in Hz

// LCD
#define LCD_REFRESH_FREQUENCY   10                     // LCD refresh frequency in Hz

// Buttons
#define BUTTON_SCAN_FREQUENCY   1000                   // Button scan frequency in Hz
#define BUTTON_SCAN_INTERVAL    (1000/BUTTON_SCAN_FREQUENCY) // Button scan interval in ms
#define BUTTON_DEAD_TIME        25                     // Button dead time in ms
#define BUTTON_WINDOW           250                    // Button window time in ms
#define BUTTON_LONG_TIMEOUT     1000                   // Button long press timeout in ms

// UART
#define UART_REFRESH_FREQUENCY  50                     // UART refresh frequency in Hz
#define UART_BAUD_RATE          115200                 // UART baud rate
#define UART_MODE               (UART_CONFIG_PAR_NONE | UART_CONFIG_STOP_ONE | UART_CONFIG_WLEN_8) // UART mode configuration

// Encoder - Theta
#define ENCODER_T_FREQUENCY     200                     // Encoder scan frequency
#define ENCODER_T_PPR           4000                    // Encoder maximum counter value
#define ENCODER_T_CAL_CYCLES    10                      // Oscillations required for calibration

// Encoder - X
#define ENCODER_X_FREQUENCY     200                     // Encoder scan frequency
#define ENCODER_X_PPR           83300                   // Encoder maximum counter value
#define ENCODER_X_INITIAL_KV    0.002272                // Initial KV value. Will be adjusted after calibration

// RGB LED
#define RGB_PWM_FREQ            1000                    // RGB LED PWM frequency in Hz
#define RGB_REFRESH_FREQUENCY   10                      // RGB LED refresh frequency in Hz

// Motor
#define MOTOR_VEL_CAL           0.25                     // Velocity during axis calibration [0.0-1.0]

// X-axis
#define X_VALUE_TOTAL_M         0.4037F                 // Maximum travel distance in m
#define X_VALUE_ABS_M           (X_VALUE_TOTAL_M/2)     // Axis limits in m (-X_VALUE_ABS_M to X_VALUE_ABS_M)

// Theta-axis
#define T_VALUE_MAX_RAD         (2*PI)                  // Maximum angle in radians
#define T_VALUE_ABS_MAX         PI                      // Axis limits in radians (-T_VALUE_ABS_MAX to T_VALUE_ABS_MAX)

// ------------------------------------------------------------------------------------------------------- //
// Hardware defines
// ------------------------------------------------------------------------------------------------------- //

// LCD
#define LCD_SSI_PERIPH          SYSCTL_PERIPH_SSI0     // LCD SSI peripheral
#define LCD_SCLK_PERIPH         SYSCTL_PERIPH_GPIOA    // LCD SCLK GPIO peripheral
#define LCD_DN_PERIPH           SYSCTL_PERIPH_GPIOA    // LCD DN GPIO peripheral
#define LCD_SCE_PERIPH          SYSCTL_PERIPH_GPIOA    // LCD SCE GPIO peripheral
#define LCD_DC_PERIPH           SYSCTL_PERIPH_GPIOA    // LCD DC GPIO peripheral
#define LCD_BKL_PERIPH          SYSCTL_PERIPH_GPIOA    // LCD BKL GPIO peripheral
#define LCD_SSI_BASE            SSI0_BASE              // Base address for SSI0
#define LCD_SCLK_BASE           GPIO_PORTA_BASE        // Base address for SCLK GPIO port
#define LCD_DN_BASE             GPIO_PORTA_BASE        // Base address for DN GPIO port
#define LCD_SCE_BASE            GPIO_PORTA_BASE        // Base address for SCE GPIO port
#define LCD_DC_BASE             GPIO_PORTA_BASE        // Base address for DC GPIO port
#define LCD_BKL_BASE            GPIO_PORTA_BASE        // Base address for BKL GPIO port
#define LCD_SCLK_CFG            GPIO_PA2_SSI0CLK       // Pin mux configuration for SCLK
#define LCD_DN_CFG              GPIO_PA5_SSI0TX        // Pin mux configuration for DN
#define LCD_SCLK_PIN            GPIO_PIN_2             // SCLK pin
#define LCD_DN_PIN              GPIO_PIN_5             // DN pin
#define LCD_SCE_PIN             GPIO_PIN_4             // EN pin
#define LCD_DC_PIN              GPIO_PIN_3             // DC pin
#define LCD_BKL_PIN             GPIO_PIN_6             // BKL pin

// Buttons
#define BUTTON_GPIO_PERIPH      SYSCTL_PERIPH_GPIOF    // Button GPIO peripheral
#define BUTTON_GPIO_BASE        GPIO_PORTF_BASE        // Base address for Button GPIO port
#define BUTTON_PIN_1            GPIO_PIN_4             // Button 1 pin
#define BUTTON_PIN_2            GPIO_PIN_0             // Button 2 pin

// UART defines
#define UART_UART_PERIPH        SYSCTL_PERIPH_UART0    // UART peripheral
#define UART_GPIO_PERIPH        SYSCTL_PERIPH_GPIOA    // UART GPIO peripheral
#define UART_UART_BASE          UART0_BASE             // Base address for UART0
#define UART_GPIO_BASE          GPIO_PORTA_BASE        // Base address for UART GPIO port
#define UART_RX_CFG             GPIO_PA0_U0RX          // Pin mux configuration for UART RX
#define UART_TX_CFG             GPIO_PA1_U0TX          // Pin mux configuration for UART TX
#define UART_RX_PIN             GPIO_PIN_0             // UART RX pin
#define UART_TX_PIN             GPIO_PIN_1             // UART TX pin

// Encoder defines - Theta
#define ENCODER_T_QEI_PERIPH    SYSCTL_PERIPH_QEI1     // QEI peripheral for Theta encoder
#define ENCODER_T_GPIO_PERIPH   SYSCTL_PERIPH_GPIOC    // GPIO peripheral for Theta encoder
#define ENCODER_T_QEI_BASE      QEI1_BASE              // Base address for Theta QEI module
#define ENCODER_T_GPIO_BASE     GPIO_PORTC_BASE        // Base address for Theta GPIO port
#define ENCODER_T_A_CFG         GPIO_PC5_PHA1          // Pin mux configuration for Theta encoder Phase A
#define ENCODER_T_B_CFG         GPIO_PC6_PHB1          // Pin mux configuration for Theta encoder Phase B
#define ENCODER_T_A_PIN         GPIO_PIN_5             // Theta encoder Phase A pin
#define ENCODER_T_B_PIN         GPIO_PIN_6             // Theta encoder Phase B pin
#define ENCODER_T_CFG           QEI_CONFIG_NO_SWAP     // Theta encoder configuration

// Encoder defines - X
#define ENCODER_X_QEI_PERIPH    SYSCTL_PERIPH_QEI0     // QEI peripheral for X encoder
#define ENCODER_X_GPIO_PERIPH   SYSCTL_PERIPH_GPIOD    // GPIO peripheral for X encoder
#define ENCODER_X_QEI_BASE      QEI0_BASE              // Base address for X QEI module
#define ENCODER_X_GPIO_BASE     GPIO_PORTD_BASE        // Base address for X GPIO port
#define ENCODER_X_A_CFG         GPIO_PD6_PHA0          // Pin mux configuration for X encoder Phase A
#define ENCODER_X_B_CFG         GPIO_PD7_PHB0          // Pin mux configuration for X encoder Phase B
#define ENCODER_X_A_PIN         GPIO_PIN_6             // X encoder Phase A pin
#define ENCODER_X_B_PIN         GPIO_PIN_7             // X encoder Phase B pin
#define ENCODER_X_CFG           QEI_CONFIG_NO_SWAP     // X encoder configuration
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

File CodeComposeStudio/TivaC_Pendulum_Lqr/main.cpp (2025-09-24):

// ------------------------------------------------------------------------------------------------------- //
// Pendulum on a cart
// ------------------------------------------------------------------------------------------------------- //

// Version: 1.0
// Author: Renan Duarte
// E-mail: duarte.renan@hotmail.com
// Date:   13/05/2024
// Device: CORTEX M4F TM4C123GH6PM Tiva C Launchpad

// ------------------------------------------------------------------------------------------------------- //
// Includes
// ------------------------------------------------------------------------------------------------------- //

// Application defines
#include "main.hpp"

// ------------------------------------------------------------------------------------------------------- //
// Functions Prototypes
// ------------------------------------------------------------------------------------------------------- //

// Send device info via UART
void DeviceUpdateUart();

// LCD update
void DeviceUpdateLcd();

// RGB LED update
void DeviceUpdateRgb();

// Button 1 event handler
void DeviceUpdateButton1 ();

// Button 2 event handler
void DeviceUpdateButton2 ();

// Control loop
void DeviceUpdateControl();

// SysTick interrupt service routine
void IsrSysTick ();

// ------------------------------------------------------------------------------------------------------- //
// Objects
// ------------------------------------------------------------------------------------------------------- //

// Display object - From Lcd_TivaC class
Lcd Display;

// Button objects - From Button_TivaC class
Button Button1, Button2;

// UART object - From Uart_TivaC class
Uart Serial;

// Encoder objects - From Encoder_TivaC class
Encoder EncoderT, EncoderX;

// RGB LED object - From Rgb_TivaC class
Rgb Led;

// Motor object - From DCMotor_TivaC class
DCMotor Motor;

// Cart PID controller object - From Pid_TivaC class
Pid ControllerCartPid;

// Cart lead controller object - From Lead_TivaC class
Lead ControllerCartLead;

// Pendulum PID controller object - From Pid_TivaC class
Pid ControllerPendPid;

// Full state LQR controller object - From StateFeedback_TivaC class
StateFeedback ControllerFullLqr;

// ------------------------------------------------------------------------------------------------------- //
// Variables
// ------------------------------------------------------------------------------------------------------- //

// Cart-related variables
volatile cart_t Cart = cart_t_default;

// Pendulum-related variables
volatile pendulum_t Pendulum = pendulum_t_default;

// Calibration variables
volatile calibration_t CalT = {.Status = CAL_PENDING, .Progress = 0, .Offset = 0, .Max = ENCODER_T_PPR, .Kv = 1};
volatile calibration_t CalX = {.Status = CAL_PENDING, .Progress = 0, .Offset = 1000, .Max = ENCODER_X_PPR, .Kv = ENCODER_X_INITIAL_KV};

// Control mode
volatile control_mode_t ControlMode = CONTROL_OFF;

// Cart position reference - Shadow value
volatile float PosRefShadow = 0;

// Global counters
volatile uint32_t SysTickCounter = 0;
volatile uint32_t ControlCounter = 0;
volatile uint32_t UartCounter = 0;
volatile uint32_t LcdCounter = 0;
volatile uint32_t RgbCounter = 0;
volatile uint32_t ButtonCounter = 0;
volatile uint32_t EncoderTCounter = 0;
volatile uint32_t EncoderXCounter = 0;

// Intervals
const uint32_t ControlInterval = TIMER_FREQUENCY / CONTROL_LOOP_FREQUENCY;
const uint32_t UartInterval = TIMER_FREQUENCY / UART_REFRESH_FREQUENCY;
const uint32_t LcdInterval = TIMER_FREQUENCY / LCD_REFRESH_FREQUENCY;
const uint32_t RgbInterval = TIMER_FREQUENCY / RGB_REFRESH_FREQUENCY;
const uint32_t ButtonInterval = TIMER_FREQUENCY / BUTTON_SCAN_FREQUENCY;
const uint32_t EncoderTInterval = TIMER_FREQUENCY / ENCODER_T_FREQUENCY;
const uint32_t EncoderXInterval = TIMER_FREQUENCY / ENCODER_X_FREQUENCY;

// Full PID controller - Weigth of each PID - Card and Pendulum
float PidCartWeigth = 0.2;
float PidPendWeigth = 0.8;

// ------------------------------------------------------------------------------------------------------- //
// Update cart state based on encoder readings
// ------------------------------------------------------------------------------------------------------- //
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

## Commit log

2024-06-02 Adjusting calibration
    [BOM.xlsx, Debug.xlsx, Steps_Cart_Acc.xlsx]
2024-07-23 Added more controllers
    [Debug.xlsx]
2024-08-20 Major updates
    [180.xlsx, 20.xlsx, 40.xlsx, 80.xlsx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]
2025-09-04 Update before switch to DC motor
